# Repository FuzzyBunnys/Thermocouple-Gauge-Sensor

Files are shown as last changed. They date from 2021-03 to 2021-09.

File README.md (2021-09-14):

# Thermocouple Gauge Sensor
This is a project detailing a project to build a measurement computer for a thermocouple vacuum gauge that is attached to a vacuum chamber. See the [GitHub pages for more information](https://fuzzybunnys.github.io/Thermocouple-Gauge-Sensor/). 
- The BOM is the bill of materials
- The documentation file is a word document containing technical information and context
- VacuumSensorV2 is the Mecrisp-Stellaris code
- Calibration Curve is an excel file that models the curve used to generate pressure measurements
- The Thermocouple Gauge folder contains all the Kicad files related to PCB layout and design

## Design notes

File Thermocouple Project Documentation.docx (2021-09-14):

Vacuum Thermocouple Gauge

Nicolas Krause

Introduction:

This document describes the implementation of the Vacuum Thermocouple Gauge for my Fusor. It is made up of 4 separate components, the circuit, software, vacuum gauge and PCB.

Circuit:

A non-inverting amplifier built around a TLV2461 op-amp amplifies the signal from the vacuum gauge so that a microcontroller can measure it using an ADC. The implementation is inspired by the Bell Jar’s (http://www.belljar.net/tcgauge.htm) original article.

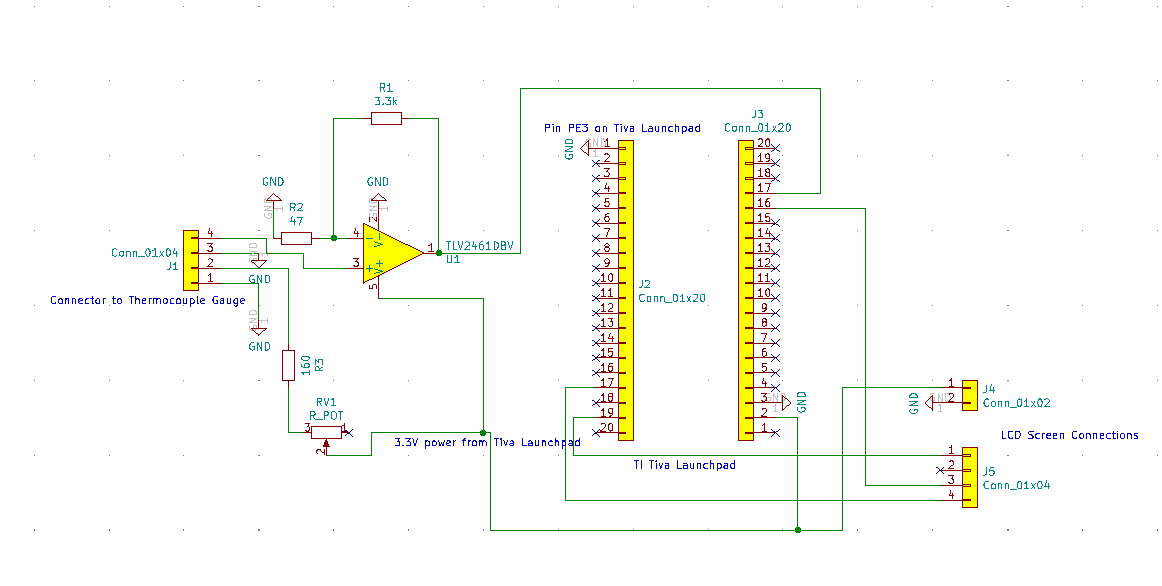
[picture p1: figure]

My circuit implementation uses a non-inverting amplifier circuit and the TLV2461 device below.

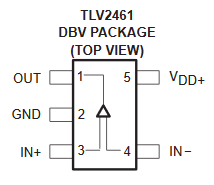
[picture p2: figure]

V_o =V_i (1+(R_f)/(R_i))=V_i (1+(3.3k)/47)=71.2V_i

The full schematic is viewable in the KiCad files. Given the values for R1 = 3.307K and R2 = 42.3 Ohms respectively, the actual precise amplification for my current built board is 78.2 times the input voltage.

Software:

The microcontroller program is written in mecrisp stellaris, a dialect of Forth. It polls the amplification circuit regularly and converts the measurement into a pressure value which it then prints out to a text LCD Screen. A Tiva C Series Launchpad development board is used to handle all of the necessary tasks. The following sequence allowed me to program my Tiva C series board for the TM4C123 chip.

1. Download Mecrisp-Stellaris
2. Download TI's Uniflash
3. Connect the Tiva C series board via usb and the debug port
4. Load mecrisp-stellaris-lm4f120.bin using Uniflash on to the board
5. Make a connection at 115200 baud rate via TeraTerm to the launchpad board.
6. Reset the board and the welcome message for mecrisp stellaris should appear.

Setting up mecrisp-stellaris took a bit of doing. The correct file has to be downloaded to the board and then a serial connection (via TeraTerm) needs to be established. To ensure legible output on the serial terminal, the following settings must be used on TeraTerm:

- 115200 baud rate
- Receive: AUTO
- Transmit: CR
- Data: 8 bit

The program has a number of words (Forth’s name for functions) that implement the program. They are described below:

AVERAGE: Produces an average of 8 input values.

ADCINIT: Initializes the ADC.

ADCREAD: Reads the ADC

SPIINIT: Initializes the SPI to communicate with the LCD

SEND: Sends a value over SPI to the LCD. Values are generally written in hex as that’s how the guide for the LCD denotes them.

CONVERT: Converts a voltage measurement to a pressure value. A vacuum thermocouple gauge has a calibration curve that relates the voltage it produces to a given pressure. Given the assumed KJL 1518/ 6343 type gauge the following set of data points is used to derive an exponential model for the CONVERT word. If you have a different type of tube you have to change this obviously. This can be viewed and edited in the calibration curve excel file included in this documentation.

The first chart above displays the curve relative to the actual voltage at the ADC while the second chart displays the curve relative to the value the ADC itself would put out. Given that it can produce 4096 values and its max reference voltage is 3.3V (see pg. 810 of the uC datasheet) we have the scale below.

UPDATE: This word prints out a pressure measurement to the LCD screen

RUN: Does exactly what it says, makes the whole program do its thing.

PCB:

The PCB is designed in KiCad and is made up of two components, the connector to the vacuum gauge and a board mounting the amplification circuit and microcontroller.

Vacuum Gauge:

The current gauge installed on the fusor is a Huntington Model 1504 (sometimes also GTC-004). It has 8 pins present on the gauge tube in an octal configuration (a legacy of vacuum tubes!) but only 4 are needed for the operation of the tube itself. A diagram of the pinout is below.

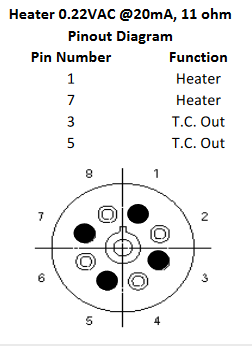
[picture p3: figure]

I guess for each of these pin connections I can hook up power and ground or sense and ground in any direction? We’ll stick to that for now.

Board Improvements:

The second revision includes a potentiometer for the power supply and a base 160 Ohm resistor to prevent filament burnout.

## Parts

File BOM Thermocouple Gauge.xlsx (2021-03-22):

Vacuum Thermocouple Gauge
Part | Quantity | Cost | Total | Digikey Part Number | Newark Part Number | Link
PCB | 3 |  | 0 | n/a |  | https://oshpark.com/
Octal Connector | 2 | 10 | 20 | Ebay |  | https://www.ebay.com/itm/2pc-bakelite-octal-8pin-tube-base-for-6sn7-el34-power-plug/193443905171
LCD Screen | 1 |  | 0 | n/a |  | https://www.sparkfun.com/products/16397
Single pin header strip | 1 |  |  |  | Any generic strip for pin connection will work, need 6 pins total (4 and 2)
TLV2461 - op amp | 5 | 2.8 | 14 | 296-7479-1-ND |  | https://www.digikey.ca/en/products/detail/texas-instruments/TLV2461CDBVT/306306
R1 - 3.3K | 1 |  | 0 |  | 603 SM size | Generic
R2 - 47 | 1 |  | 0 |  | 603 SM size | Generic
R3 - 160 | 1 |  | 0 |  | 603 SM size | Generic
RV1 - 1K | 1 |  | 0 |  | 10 Turn Pot | Generic
20 pin TI Connectors (2x10) | 2 |  | 0 |  | SSW-110-23-S-D | 0.100" spacing for rows and pins | Samtec 2x10 header
J1- Screw Terminal | 1 |  | 0 |  |  | Generic
TI Tiva C Launchapad | 1 |  | 0 |  |  | https://www.ti.com/tool/EK-TM4C123GXL

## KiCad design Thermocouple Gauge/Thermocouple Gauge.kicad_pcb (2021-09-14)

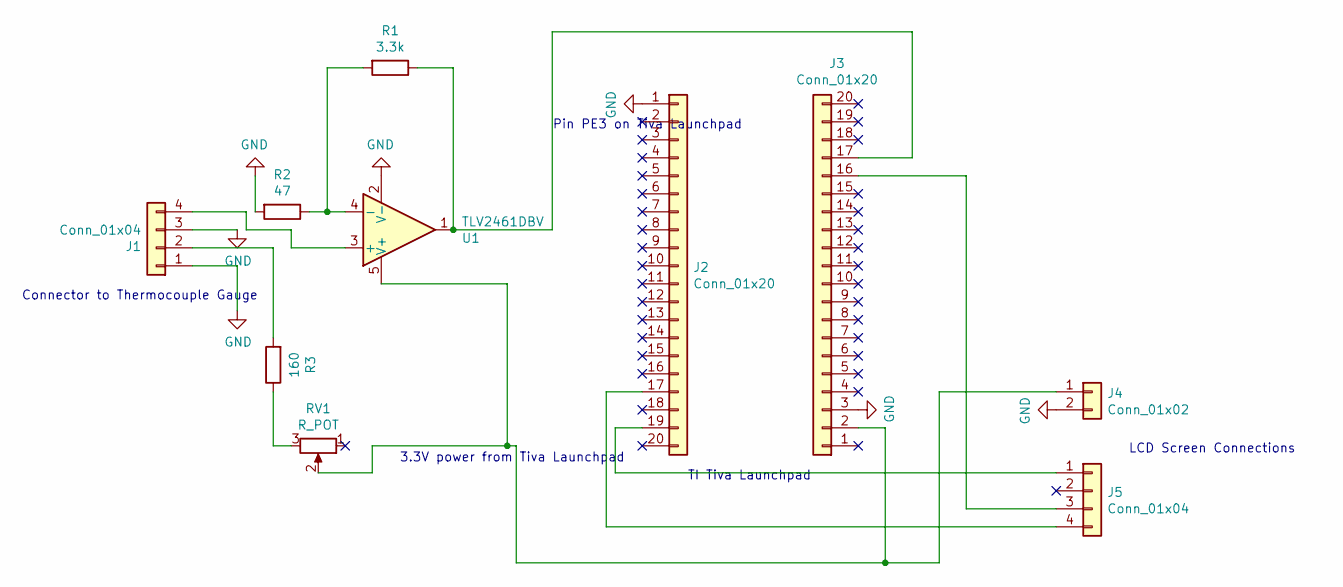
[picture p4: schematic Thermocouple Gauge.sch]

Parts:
J1: Conn_01x04; TerminalBlock_bornier-4_P5.08mm
J2, J3: Conn_01x20; SDL-120-X-XX_2x10
J4: Conn_01x02; PinHeader_1x02_P2.54mm_Vertical
J5: Conn_01x04; PinHeader_1x04_P2.54mm_Vertical
R1: 3.3k; R_0603
R2: 47; R_0603
R3: 160; R_0603
RV1: R_POT; Potentiometer_Trimmer_Bourns_3296W
U1: TLV2461DBV; SOT-23-5

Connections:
GND: J1.1, J1.3, J2.1, J3.3, J4.2, R2.2, U1.2 (V-)
unnamed: J1.2, R3.2
unnamed: J1.4, U1.3 (+)
unnamed: J2.17, J5.4
unnamed: J2.19, J5.1
unnamed: J3.2, J4.1, RV1.2, U1.5 (V+)
unnamed: J3.16, J5.3
unnamed: J3.17, R1.1, U1.1
unnamed: R1.2, R2.1, U1.4 (-)
unnamed: R3.1, RV1.3

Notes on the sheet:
TI Tiva Launchpad
Connector to Thermocouple Gauge
Pin PE3 on Tiva Launchpad
3.3V power from Tiva Launchpad
LCD Screen Connections

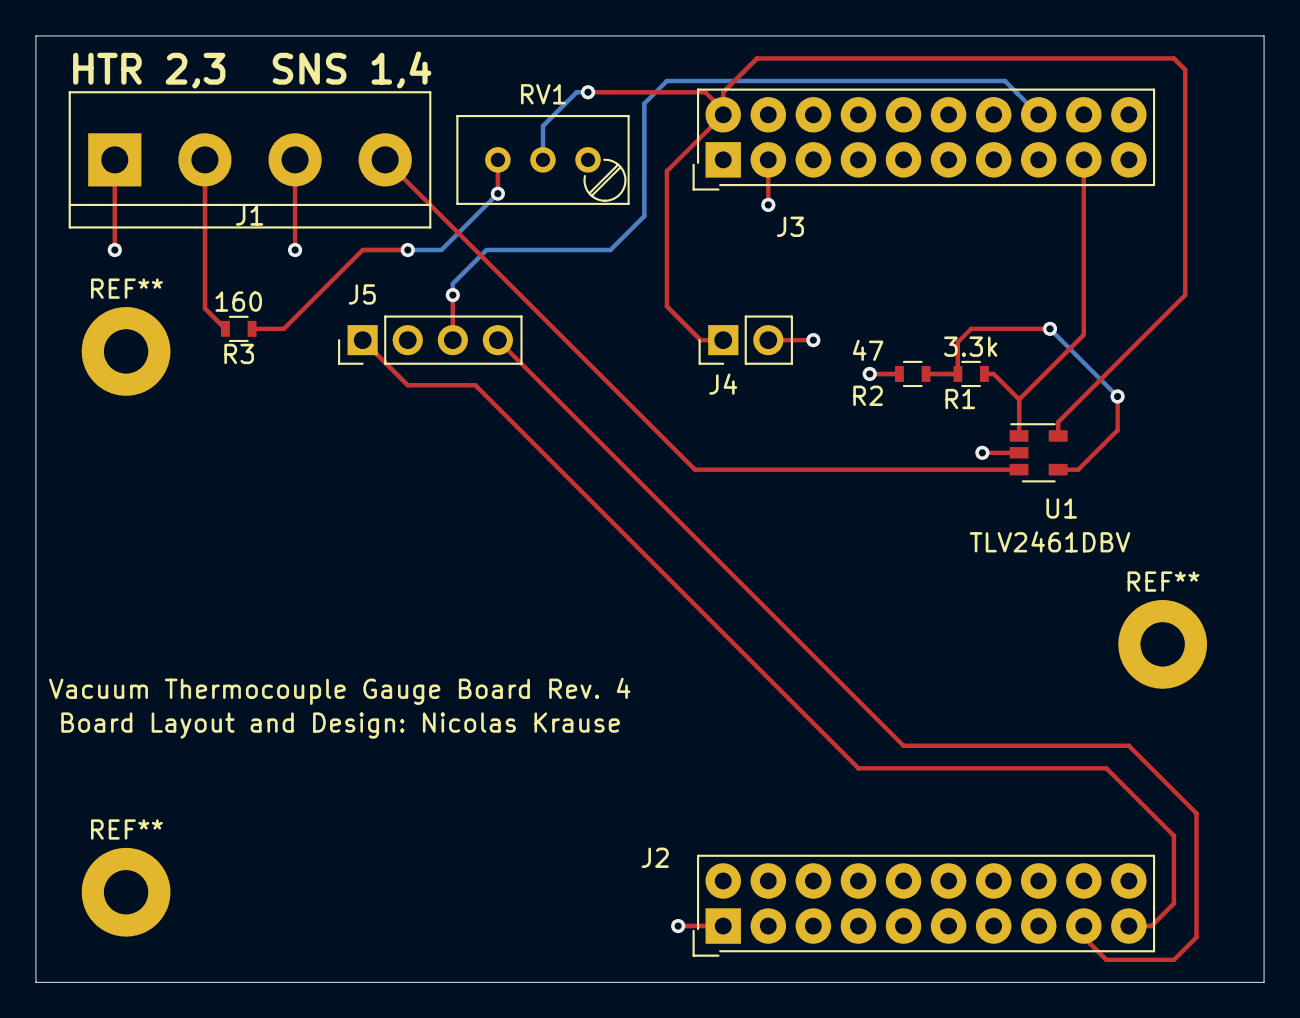
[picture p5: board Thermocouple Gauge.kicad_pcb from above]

Board: 2 copper layers, 69.2 x 53.3 mm, 10 parts (0 on the bottom side), 10 nets.

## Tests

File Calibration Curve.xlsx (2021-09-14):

TC Max V | 0.01 |  |  | Amplification | 71.2
ADC Scale | 0.0008056640625
Voltage % | Voltage V | Amp Voltage | ADC Output | Pressure (mTorr)
1 | 0.01 | 0.712 | 883.7430303 | 0.001
0.989 | 0.00989 | 0.704168 | 874.021857 | 1
0.917 | 0.00917 | 0.652904 | 810.3923588 | 5
0.85 | 0.0085 | 0.6052 | 751.1815758 | 10
0.736 | 0.00736 | 0.524032 | 650.4348703 | 20
0.65 | 0.0065 | 0.4628 | 574.4329697 | 30
0.574 | 0.00574 | 0.408688 | 507.2684994 | 40
0.522 | 0.00522 | 0.371664 | 461.3138618 | 50
0.367 | 0.00367 | 0.261304 | 324.3336921 | 100
0.227 | 0.00227 | 0.161624 | 200.6096679 | 200
0.166 | 0.00166 | 0.118192 | 146.701343 | 300
0.106 | 0.00106 | 0.075472 | 93.67676121 | 500
0.063 | 0.00063 | 0.044856 | 55.67581091 | 1000

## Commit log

2021-03-22 Add files via upload
    First commit of PCB files
    [Thermocouple Gauge-B_Cu.gbr, Thermocouple Gauge-B_Mask.gbr, Thermocouple Gauge-B_SilkS.gbr, Thermocouple Gauge-Edge_Cuts.gbr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]
2021-09-14 Add files via upload
    PCB layout, schematic and gerbers.
    [Thermocouple Gauge-B_Cu.gbr, Thermocouple Gauge-B_Mask.gbr, Thermocouple Gauge-B_SilkS.gbr, Thermocouple Gauge-Edge_Cuts.gbr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]
